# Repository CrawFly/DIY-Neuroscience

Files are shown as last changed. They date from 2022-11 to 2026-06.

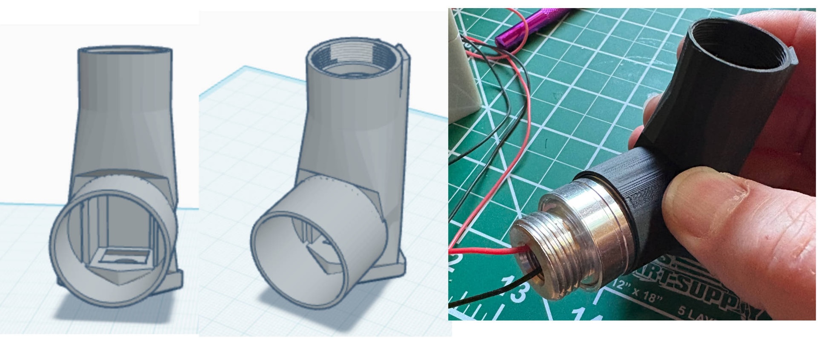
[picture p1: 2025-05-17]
OFM LED parts/OFM LED.jpg

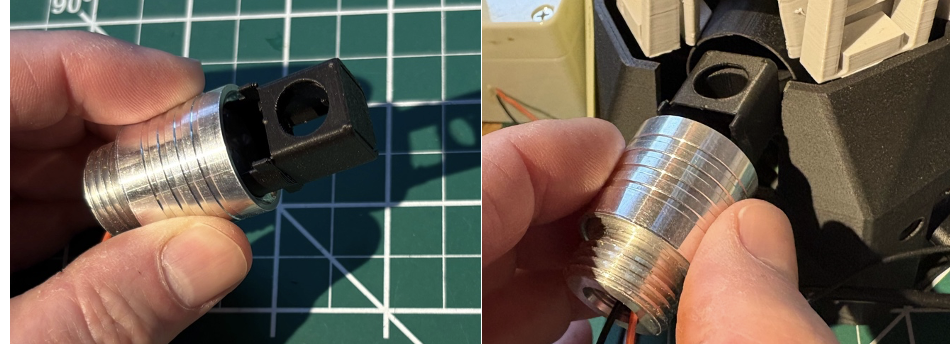
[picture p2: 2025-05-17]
OFM LED parts/OFM LED Filter cube.png

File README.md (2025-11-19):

# DIY-Neuroscience
This is a repository for storing code, stl files, and build instructions for DIY neuroscience equipment designed and built by faculty at Cornell University and Hobart &amp; William Smith Colleges.

Build videos for the micromanipulator builds can be found on our YouTube Channel at:
https://www.youtube.com/@jimryan4024
These build videos are too large to include here.

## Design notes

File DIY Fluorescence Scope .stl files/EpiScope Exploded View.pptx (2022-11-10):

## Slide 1

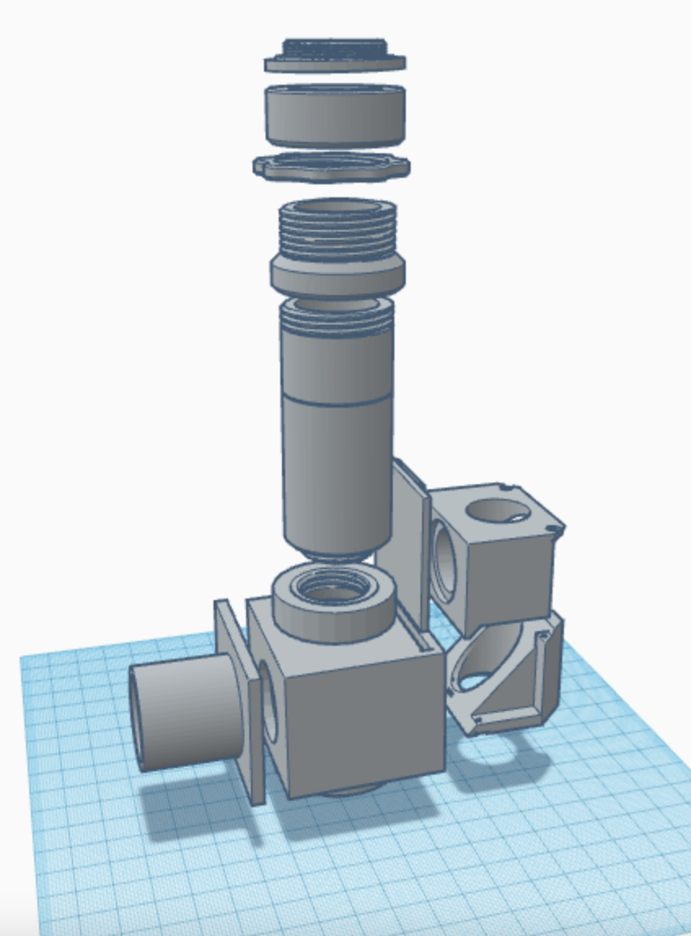
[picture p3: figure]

EpiScope
Exploded View

C-Mount Collar (B)

C-Mount Lock Nut (C)

Tube Extender Ring (D)

Microscope Tube (E)

Filter Cube Door (J)

Microscope Tube
Lower Adapter (F)

Filter Cube Top (K)

LED Tube (I)

Filter Cube
Holder (G)

Filter Cube Bottom (L)

RMS Objective
Lens Adapter (H)

C-Mount Thread (A)

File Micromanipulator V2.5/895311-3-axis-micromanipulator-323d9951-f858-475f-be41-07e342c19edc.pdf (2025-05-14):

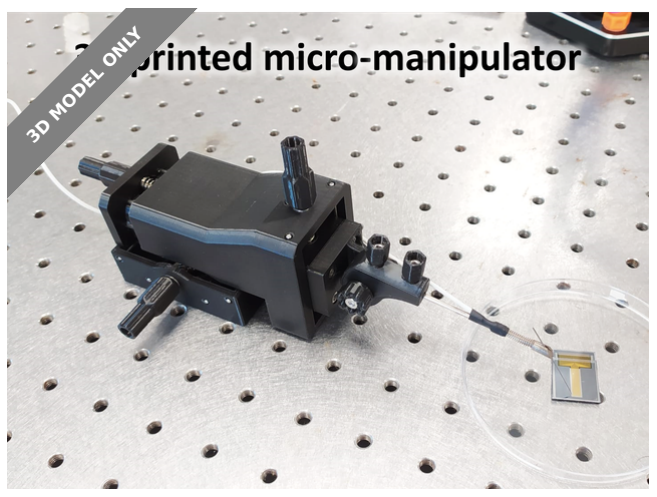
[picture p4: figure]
3D MODEL ONLY

## Summary

This design is a micromanipulator designed to precisely handle tools at the micron scale

Hobby & Makers (https://printables.com/model?categoryId=48) > Tools (https://printables.com/model?categoryId=49)

Tags: | precision | linearmotion | handler | micron | manipulator
micromanipulator | microscopic

Micromanipulators are tools designed to precisely handle objects at the micron scale. They are very important in science as they allow to interact directly with microscopic device, when direct manual handling would most likely result in destruction. However, professional quality micromanipulator can be very expensive (thousands of USD), out of reach of hobbyists and sometimes a scarce resource even for professional researchers.

This is my take at designing a high quality micromanipulator. The result is stiff, compact and moves smoothly. Not quite up to par with the commercial alternatives, but fit for most applications and accessible for a handful of USD and half an hour of your time.

The complete build process is described in detail in an instructable:

https://www.instructables.com/Build-a-3D-Printed-Micro-manipulator/

RemiRafael (https://printables.com/@RemiRafael)

## 3 axis micromanipulator

VIEW IN BROWSER (https://printables.com/model/895311-3-axis-micromanipulator)

updated 29. 5. 2024 | published 29. 5. 2024

## Model files

micromanipulator-z-slider.stl

micromanipulator-middle.stl

micromanipulator-base.stl

straight-holder-base.stl

straight-holder-arm.stl

micromanipulator-top.stl

straight-holder-knob.stl

knob.stl

cutting-guide-micromanipulator.stl

## License

This work is licensed under a
Creative Commons (4.0 International License)

Attribution-NonCommercial (http://creativecommons.org/licenses/by-nc/4.0/)

✖ | Sharing without ATTRIBUTION
✔ | Remix Culture allowed
✖ | Commercial Use
✖ | Free Cultural Works
✖ | Meets Open Definition

holder-knob.stl

90-holder.stl

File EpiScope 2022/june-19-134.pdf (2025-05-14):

The Journal of Undergraduate Neuroscience Education (JUNE), Fall 2020, 19(1):A134-A140

JUNE is a publication of Faculty for Undergraduate Neuroscience (FUN) www.funjournal.org

## ARTICLE Building Your Own Neuroscience Equipment: A Precision Micromanipulator and an Epi-fluorescence Microscope for Calcium Imaging

### James Ryan¹, Bruce R. Johnson², and David Deitcher²

1Biology Department, Hobart and William Smith Colleges, Geneva, NY 14456; 2Department of Neurobiology and Behavior, Cornell University, Ithaca, NY 14853.

A faculty member’s ability to develop meaningful research-oriented laboratories in neurobiology is often hampered by
the rapid pace of new technologies and the increasing cost of equipment. To help undergraduate neuroscience faculty meet these challenges, we introduce two important neuroscience research tools we designed and built. The first is a precision micromanipulator for neurophysiology applications costing less than $40 USD. We compare data generated using the DIY manipulator with commercial micromanipulators costing over $1000. The second tool is our newly designed 3D printed epi-fluorescence microscope. Commercial fluorescence imaging devices often cost over $20,000, but our 3D printed version is constructed for less than $1200. This epi-fluorescence microscope uses interchangeable LED light sources and filter sets to image static fluorescence in prepared slides and calcium imaging of neuronal activity in living Drosophila brains. This later technique uses transgenic flies with a genetically encoded calcium indicator, GCaMP, linked to green fluorescent protein (GFP). During an action potential, calcium ions (Ca²⁺) enter neurons and are observed as an increase in fluorescence intensity from a series of video images. These neuronal firing patterns can be assessed qualitatively and quantitatively to understand neural circuits leading to specific behaviors. We plan to develop curricula around the use of the epi-fluorescence microscope for calcium imaging in the next year, and to provide detailed parts sources and construction guides for the student and faculty DIY experience.

Key words: micromanipulator; neurophysiology; epsp; epi-fluorescence; GFP; mCherry; GCaMP; Calcium imaging

This report is based on our presentation at the 2020 FUN Virtual Meeting where we introduced two new teaching and research tools for undergraduate neuroscience faculty. The rapid pace of new technologies and the increasing cost of equipment can restrict the development of meaningful research-oriented laboratories in neuroscience. However, the present availability of inexpensive industrial parts, efficient supply chains for parts distribution, 3-D printing and open source software development can facilitate faculty development of do-it-yourself (DIY) laboratory teaching and research tools to overcome curricular and research financial limitations.
Previously the Cornell Hoy Neurobiology group and collaborators have designed a variety of inexpensive or free tools for neuroscience teaching and research laboratories. These include an extracellular amplifier (Land et al., 2001), suction electrodes (Land et al., 2001; Johnson et al., 2007), a temperature control device (Krans and Hoy, 2005), micromanipulators (Krans et al., 2006), physiological stimulators (Land et al., 2004), LED control boxes for optogenetic stimulation (Pulver et al., 2010; Vilinsky et al., 2018), and electrophysiological data acquisition and analysis software (Lott et al., 2009). Here we describe our
recent | progress | developing | an | inexpensive
micromanipulator for student neurobiology teaching labs and research, and an inexpensive fluorescence imaging device for dynamic and static fluorescence visualization. Precision micromanipulators from commercial sources cost ~$500 to over $1000 USD. The one described below can be constructed by faculty or students for about $40.00 in parts. Fluorescence microscopes with imaging cameras are expensive, often costing over $20,000 each. This cost often puts fluorescence microscopes out of reach for many undergraduate neuroscience courses and faculty/student research. Our imaging microscope can be constructed using about $1200 in parts. A major goal for our DIY work is to increase the toolbox for neuroscience teaching, learning and research for students and faculty, especially at national and foreign institutions with limited financial resources.

### DIY EQUIPMENT

Precision Micromanipulator Design
We designed an inexpensive micromanipulator that student lab teams could assemble from a kit and use for any laboratory exercise or research that requires fine probe placement. The precision micromanipulator can be built in approximately one hour. It consists of two modified x-y microscope stages, several 3D printed parts, and various nuts and bolts (Figure 1). The two x-y mechanical stages can be purchased online (Amazon, eBay) for under $20USD each. These stages have movement range of 60mm x 30mm and an accuracy of 0.1mm. The manipulator is constructed by first removing the slide holders from both x-y stages and then removing the y-axis from the x-axis on one of the two stages. The single x-axis is joined to the other x-y stage using an aluminum L-bracket with M3 screws and nuts. Finally, the completed x-y-z stage is epoxied and

Ryan et al. | DIY Neuroscience Equipment | A135

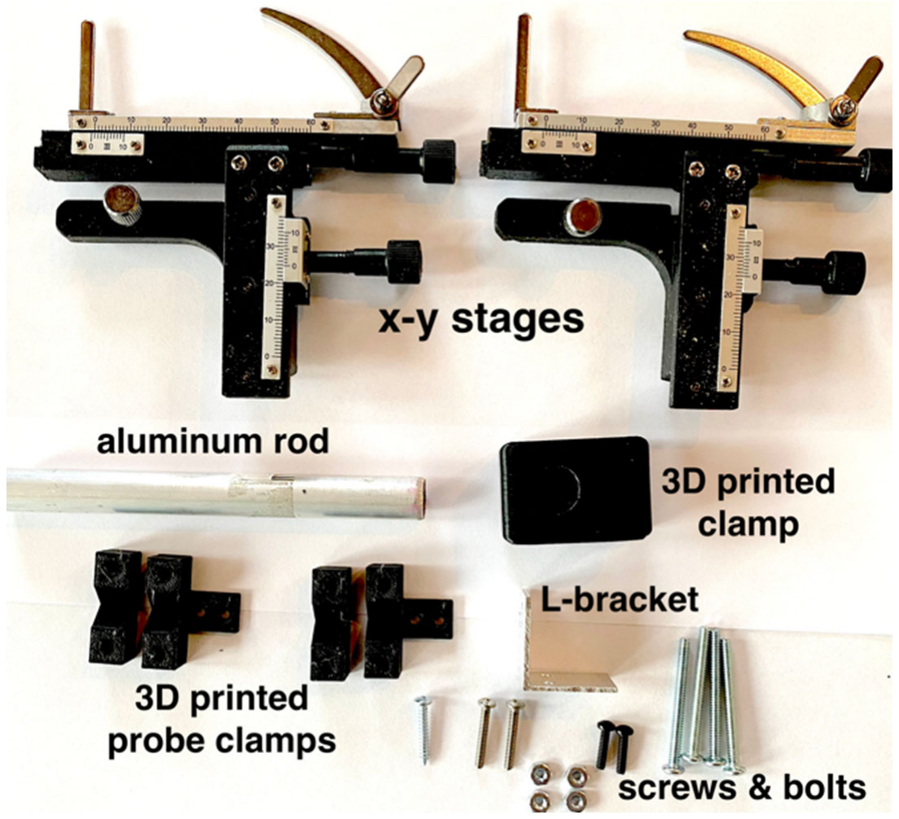
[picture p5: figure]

Figure 1. The components for assembling the DIY precision micromanipulator. There are 2 x-y mechanical stages, an aluminum rod and L-bracket, a set of 3D printed parts, and miscellaneous nuts and bolts for assembly.

screwed into the 3D printed manipulator clamp. The 3D printed parts include a manipulator clamp, a thumb screw housing, and a set of 4 probe holder clamps (Figure 2). These parts are printed from .stl files using PLA, ABS, or similar filaments at 80% infill for added strength. The .stl files can be sent to a local 3D printer or uploaded to an online printing service such as CraftCloud. The 3D printed thumb screw is both threaded into the M6 hex cap and epoxied in place. The completed thumb screw is then threaded into a nut housed inside the 3D printed manipulator clamp. We are preparing parts lists, construction manuals and videos for future dissemination.

DIY Micromanipulator Performance
We compared the stability and fine movement accuracy of our DIY manipulator with a much more expensive (~$1300) Narishige M333 micromanipulator that is normally used for student electrophysiological recordings in the “Principles of Neurophysiology“ laboratory class at Cornell University (BioNB4910). A conventional electrophysiological rig (Wyttenbach et al., 2018) with 2 A-M Systems Model 1600 intracellular amplifiers, an ADInstruments Power Lab for data acquisition with LabChart software, and glass intracellular microelectrodes filled with 3M KCl (resistances 15-20 MOhm) were used to record and display the membrane potentials from crayfish muscle fibers. We recorded intracellular excitatory synaptic potentials (EPSPs) from two different crayfish superficial flexor (SF) muscle fibers with electrodes and amplifier headstages clamped to our DIY and the Narishige manipulators. Details of the saline composition, dissection and recording protocols for crayfish muscle are found in the Crawdad lab manual (Wyttenbach et al., 2014)
Figure 3 shows EPSPs recorded simultaneously from different muscle fibers using the two manipulators. Both muscle fibers were easily penetrated, and both recordings were stable and of similar fidelity. Thus, the DIY manipulator has the precision and stability to record intracellular potentials. The EPSP amplitudes recorded with the Narishige M333 micromanipulator (blue trace) have higher amplitudes than those recorded with our DIY manipulator (red trace), probably because the electrode of the blue recording was closer to a synaptic site. These muscles do not fire action potentials, and EPSP amplitude decays with distance from the synaptic site (Hoyle, 1983). The red and blue recordings in Figure 3 are not the same EPSPs because the SF muscles are poly-neuronally and multiterminally innervated by different, spontaneously active motor neurons (Atwood, 2008).

Epi-fluorescence Microscope Design
The goal here was to design an affordable epi-fluorescence microscope that small student teams could also assemble from a kit and use to bring cutting edge research into the undergraduate neuroscience curriculum. To meet this goal, we designed and built an epifluorescence microscope for approximately $1200 USD. The 3D printed epi-fluorescence microscope described here is suitable for many neuroscience applications including calcium imaging in living neurons.

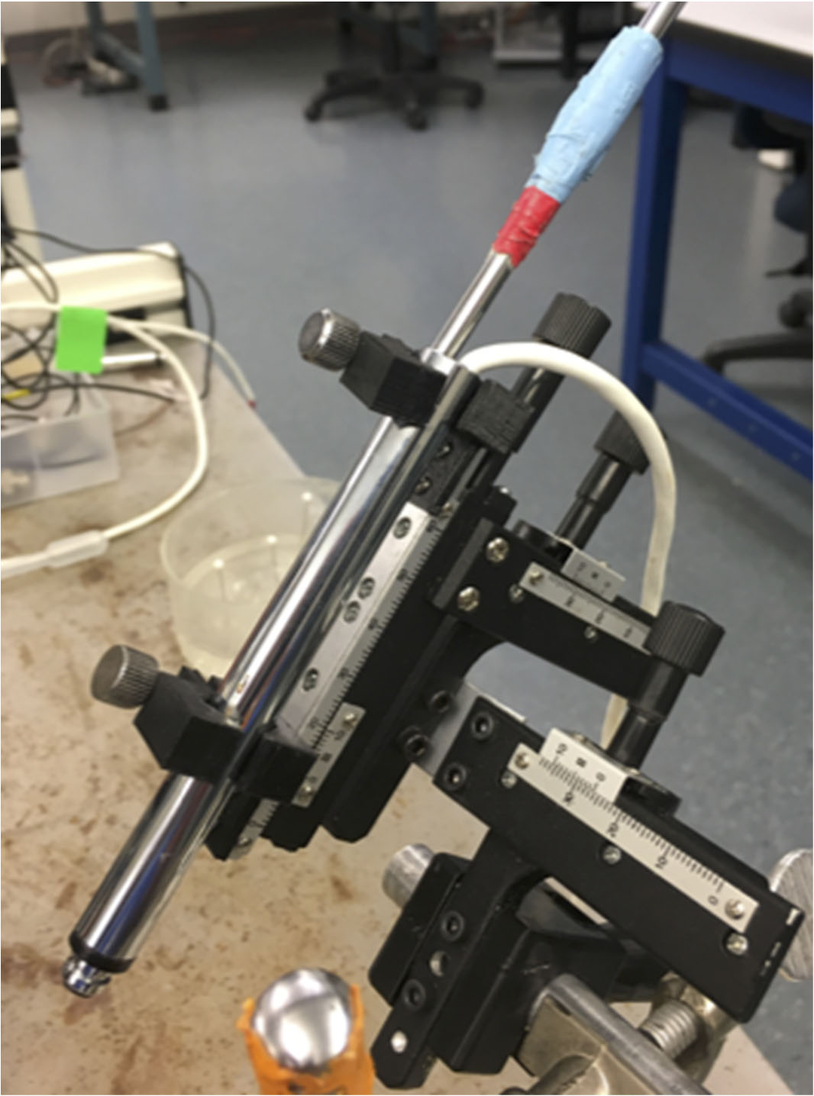
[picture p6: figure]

Figure 2. The fully assembled micromanipulator with intracellular amplifier head-stage clamped in place.

The Journal of Undergraduate Neuroscience Education (JUNE), Fall 2020, 19(1):A134-A140 A136

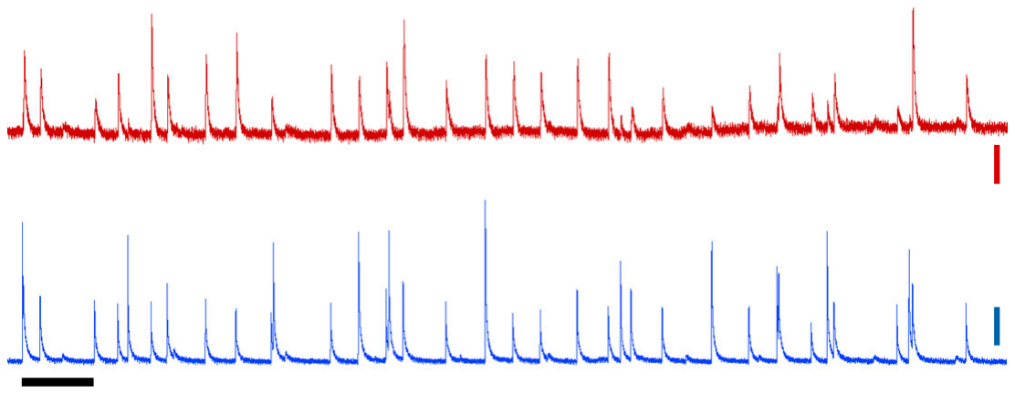
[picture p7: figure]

Figure 3. Simultaneous intracellular recordings of excitatory postsynaptic potential (EPSPs) from 2 different crayfish muscle fibers. Top red trace DIY manipulator; resting potential, -84 mV; calibration bars, 1 mV. Bottom blue trace, Narishige M3330 manipulator; resting potential, -75 mV; calibration bar, 2 mV. Note higher gain in red trace. Horizontal calibration bar, 500 ms.

The scope consists of several off the shelf components coupled with a set of 3D printed parts for the optical housing (Figure 4). The base of the scope is an aluminum optical breadboard drilled for M6 metric threads. Attached to this base is a 2x2 inch extruded aluminum column with t-slots which carries the 3D printed optical components and a precision lab jack for raising and lowering the specimen stage.
Attached to the top of the precision lab jack is a clear plexiglass plate (130 x 190 mm) that holds the specimen slide or dish. Positioning of the specimen in the x-y planes is achieved by a standard x-y mechanical microscope stage mounted to the upper surface of the plexiglass stage. The lab jack allows the entire stage assembly to be lowered easily to replace specimens or add fluids.
On the vertical column, the microscope uses a linear stage with micrometer adjustment for precision focusing the objective lens. Attached to the linear stage is the 3D printed optical housing. The main housing contains the fluorescence filters and has a male c-mount on top for attaching the CMOS camera and a female c-mount on the bottom for the 20x long working distance objective lens. The monochrome global shutter CMOS camera (~$180 from Basler, model da1280-54um/uc) is capable of acquiring images in low light at up to 54 frames per second. This camera has a resolution of 1280x960 pixels and uses a 1/3” Aptina AR0134 sensor. However, any camera with a c-mount can be attached to this port. Inside the main housing is a double filter slider that accepts two sets of fluorescence filters. The excitation and emission filters are 25mm diameter and the dichroic mirror (beamsplitter) is 25.5x36mm. The calcium imaging described below used a single band filter set tailored for green fluorescent protein (GFP) from Iridian Spectral Technologies: 469-35nm excitation, 497nm dichroic mirror, and 525-39nm emission filter ($450 USD). A second filter set for mCherry or Alexa Fluor 595 can be added to the filter slider if desired. In addition, these filter sliders are very inexpensive to 3D print, allowing the user to have several sliders and filter combinations ready to swap out in seconds.
The light source for the scope is an interchangeable highpower LED with heat sink connected to an LED controller box powered by either AC or DC and capable of being driven by a computer stimulus generator via a BNC cable (Figure

4). The wiring diagram for the LED controller has been described previously (Pulver et al., 2011 Vilinsky et al., 2018). For GFP a Cree XLamp XP-E2 high power blue (470nm peak, $4USD, LED Supply.com) LED is coupled to a BuckPuck DC LED driver ($20USD, LEDSupply.com). The LED and a 20mm narrow spot LED lens are housed in a 1 inch diameter aluminum heat sink ($15USD, LEDSupply.com). The LED and its heat sink housing are inserted into the 3D printed LED port. This design allows rapid exchange of different colored LEDs.
The 3D printed parts were designed using the free, online CAD program TinkerCad (AutoDesk). TinkerCad allows you to build complex parts from a library of basic shapes or to import and modify existing .stl files. Finished parts are exported as .stl files for 3D printing (Figure 5). The .stl files can be printed on any 3D printer. However, printing these parts using an online print company such as CraftCloud allow greater choice of print materials. The optical housing described here was printed using MJF Nylon or resin. These materials are stronger and provide higher detail than that of PLA or ABS plastics.
Finally, the microscope is modular in design. Removing the fluorescence filters and adding an LED light source from below the specimen converts the scope into a conventional light microscope. Screw a post and micromanipulator into the base and it becomes a neurophysiology rig.

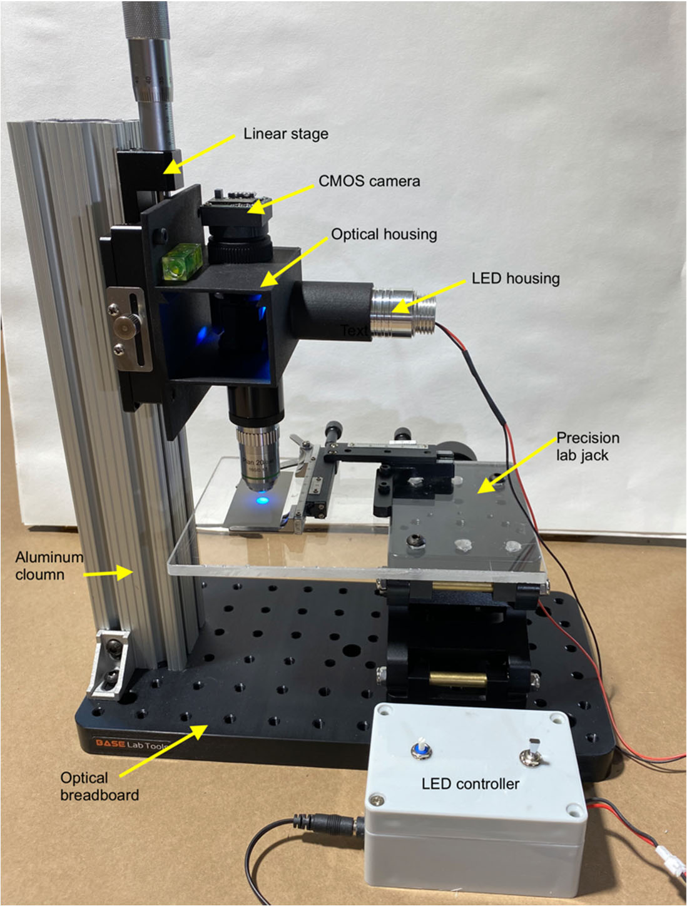
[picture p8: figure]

Figure 4. The epi-fluorescence microscope with LED controller.

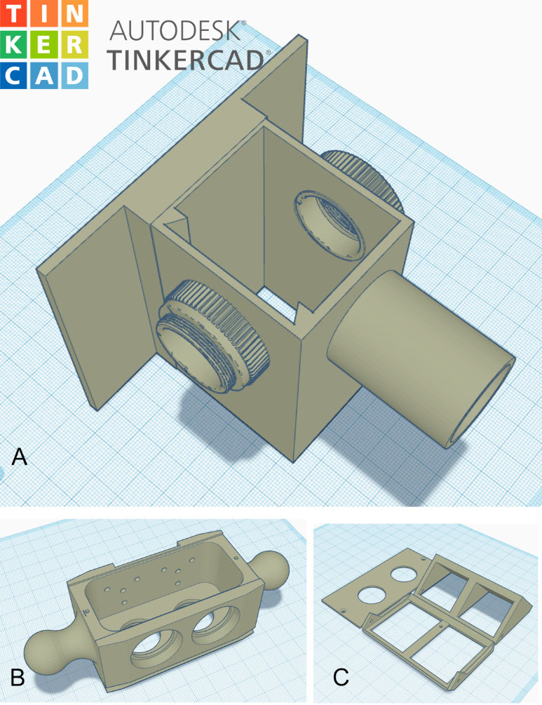
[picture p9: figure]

Figure 5. 3D printable microscope parts shown in TinkerCad prior to export as .stl files. A) Main optical housing, B) Double filter slider, and C) the filter holder components.

Fly Stocks for Imaging Preps
Fluorescent Drosophila lines were raised on standard cornmeal-molasses food. The stocks used were UAS GCaMP7b; P{GMR94G06-GAL4}attP2 for calcium imaging from the Bloomington Stock Center (#80907and #40701) and jus-GAL4 UAS-CD8-GFP (available from D. Deitcher) for static fluorescent imaging of membrane-bound GFP.

Larval and CNS Preparation
Wandering third instar larvae were selected with forceps, placed in a Sylgard petri dish and rinsed with water, then pinned at the mouth hooks and posterior end with fine insect pins with the dorsal (trachea) side oriented up. Room temperature saline (135 mM NaCl, 5 mM KCl, 2 mM CaCl2, 4 mM MgCl2, 5 mM BES, pH 7.5) for calcium imaging was added to the preparation. A superficial incision is made from the tail to the mouth hook with micro-scissors and the “guts” are carefully removed to reveal the CNS composed of brain lobes and ventral ganglion. Additional pins are placed to flatten the cuticle flaps into a “filet” (Pulver et al., 2011). For static fluorescent imaging, the Sylgard disc was adhered to a glass slide with double-sided tape and then imaged using appropriate camera settings. For dynamic calcium imaging, the CNS was excised from the larval filet and gently placed on a Sylgard-coated glass depression slide and covered with saline. The slide was placed on the microscope stage. Initially the camera was set to autoexposure to locate the preparation, then manually adjusted to reveal the GCaMP7b labeled motoneurons.

Flourescent Imaging
To test the epifluorescence microscope, we first attempted to image neurons expressing GFP in the ventral ganglion of the larva. Figure 6 shows static GFP imaging of a ventral ganglion of a third instar larva expressing the membrane-bound GFP fusion, CD8-GFP in selected neurons driven by the GAL4/UAS binary expression system. CD8-GFP is a useful label to highlight the morphology of neurons.
Next, to show the utility of the microscope we imaged a ventral ganglion expressing the calcium-sensitive protein GCaMP7b in a pair of motor neurons in each segment. Images were sent at 10 fps for 300 seconds from the camera to a lap top computer, using camera supplied software, and converted into an AVI format with Fiji (Image J) software. Figure 7 shows two frames of dynamic imaging of actively firing motor neurons in the abdominal ganglia of a fruit fly larvae from the video link (https://youtu.be/zB55QNQ_IrM). For a short while after the larval fly’s CNS is removed, CNS motor networks will produce spontaneous neural activity that is correlated with larval crawling and turning (fictive locomotion, Pulver et al., 2015). Action potential-induced
depolarization | results | in | calcium | entry

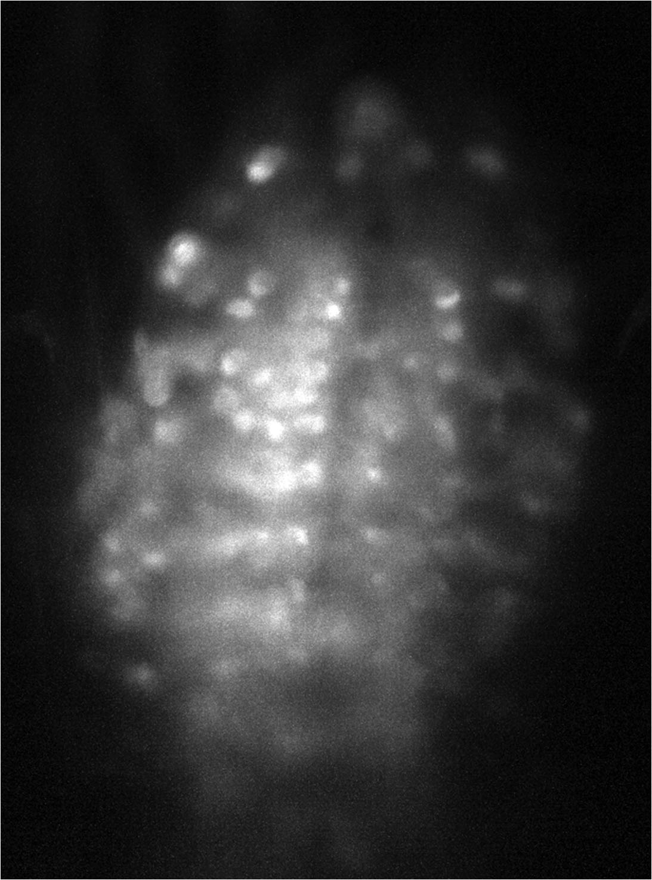
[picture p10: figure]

Figure 6. Expression of membrane-bound GFP in ventral ganglion neurons that express the neural gene, julius seizure (jus).

The Journal of Undergraduate Neuroscience Education (JUNE), Fall 2020, 19(1):A134-A140 A138
which is detected by the genetically encoded calcium indicator, GCaMP that is expressed in selective motoneurons. Thus, calcium-induced fluorescence during neural activity is a proxy for identifying actively firing neurons that normally drive muscles to execute larval locomotion. These neuronal firing patterns can be assessed qualitatively and quantitatively to understand neural circuits leading to specific behaviors.

### DISCUSSION

We present two new teaching and research tools as “proof of concept” of our recent DIY efforts to increase the faculty toolbox for neuroscience teaching, learning and research. Our DIY manipulator performed well compared to the commercial Narishige M333 when recording synaptic potentials. The DIY manipulator could be used for any student lab exercise or research that requires fine probe placement, such as for cell injection of dyes or genetic material. Although students and faculty have not yet formally tested and assessed it, initial and limited feedback for manipulator assembly and use was positive with constructive criticisms from faculty participating in the January 2020 CrawFly workshop in San Antonio. A manipulator made by one of the 2020 CrawFly participants was used to record miniature end-plate potentials from fruit fly larval muscle during the workshop (data not saved). The inexpensive manipulator could expand the range of electrophysiological exercises possible in a student/faculty lab. For example, faculty could add conventional intracellular and whole cell patch recording to student electrophysiology exercises. Our students will construct and use the DIY manipulator for electrophysiological student lab exercises. Learning outcomes, specific student skill objectives, and data analysis suggestions for our electrophysiology exercises are found in the Crawdad lab manual (Wyttenbach et al., 2014).
Our initial results of imaging static GFP fluorescence in fixed tissue and dynamic GFP fluorescence from living neurons during fictive larval locomotion (Pulver et al., 2015) show that our fluorescence microscope is operationally ready to be brought into the student laboratory classroom and into faculty research labs. Any type of fluorescence tissue could be imaged with the appropriate excitation and emission filters. Our fluorescence microscope facilitates unique and high powered research experiences for students and faculty with limited financial resources. We are not the first to propose inexpensive fluorescence imaging for the student neuroscience lab or for research. Our imaging microscope design was inspired by previous efforts including from the “FlyPi” group (Chagas et al., 2017), the miniscope produced by Zhang et al. (2019) and an imaging system recently adapted to a classroom compound microscope (Sane et al., 2020- this JUNE issue). For an imaging microscope design that fit our needs, we searched for the least expensive, yet high quality options for the microscope imaging components, light filters, camera, microscope and mounting stage parts, and JR designed the 3-D printed optical housing, filter holders, and slider.
Our student learning objectives and skills for the imaging

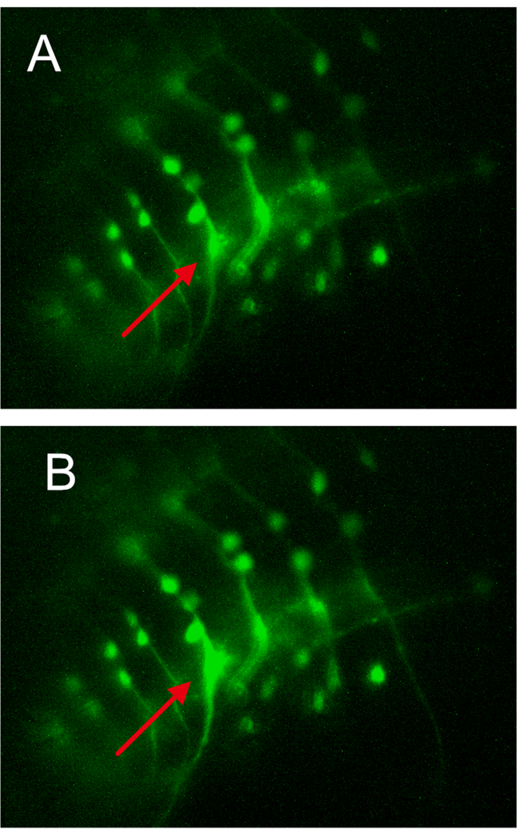
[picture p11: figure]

Figure 7. GCaMP7b fluorescence in select motoneurons of the ventral ganglion. Two single frames taken from series illustrate waves of neural activity during fictive locomotion. A. Earlier fame shows cell at red arrow with low light intensity. B. Later frame shows higher intensity light emission from the same neuron, indicating greater electrical excitability. See short video link (https://youtu.be/zB55QNQ_IrM) for entire series of images.

microscope and dynamic imaging project will promote interdisciplinary thinking and skills in our neuroscience students. For example, they will study the excitable properties of neurons though calcium imaging as a proxy for signal transmission by action potentials, and the advantages of imaging for exploring neuronal circuit activity (Yang and Yuste, 2017). Students will examine the properties of light and optics, and understand principles of fluorescence imaging (Cox, 2012) as they build and use their imaging microscopes to measure fluorescence in living preparations expressing fictive locomotion. They will learn introductory coding to control camera software and analyze images, and practice engineering design and construction by building the microscope. This includes 3D printing, soldering, fine scale assembly, and troubleshooting. Finally, students will perfect their dissection and dexterity skills by preparing Drosophila larval nervous systems for imaging.
We are still preparing imaging analysis protocols appropriate for our undergraduate student use. μManager software can be used to gather the imaging movies from the camera, and image J to process the images and select “regions of interest”. Data analysis programs such as
Dataview | (Heitler, | 2009; | https://www.st-
andrews.ac.uk/~wjh/dataview/) can be used to visualize and measure fluorescent amplitude and activity patterns (see Sane et al., 2020, this JUNE issue). Our imaging software protocols, in prep, will be designed for student interaction to modify Python code at various phases of image acquisition, analysis and visualization.
We hope that our goals for the imaging microscope project in particular will be broadly applicable at other institutions. The National Research Council (2003) emphasizes that future science research progress will require greater STEM interdisciplinary training. We plan to create an interdisciplinary classroom where students from different STEM studies work together to develop the confidence to build and understand equipment and solve biological problems. Interdisciplinary science education is considered critical for the future recruitment of talented scientists (Kazar and Elrod, 2012). Our imaging project promotes interdisciplinary learning with engineering design, physics (optics and light principles), biology (genetics and neuroscience), and computer science (introductory coding to control camera software and analyze images). Teambased learning skills required for research (Bennett and Gadlin, 2012) will be fostered as student teams build, test, and trouble shoot their own instrumentation, and gather and analyze data to answer biological questions. Too often our students treat instrumentation as a “black box”, with little understanding of how scientific equipment works. We are in the process of developing written and video guides for construction and use of the manipulator and the imaging microscope, along with laboratory modules to guide inquiry driven research experiences for students (Fromherz et al., 2018).
Our plans for a Spring 2020 rollout of student team construction and use of the manipulator and imaging microscope in the laboratory classroom were derailed by the Covid-19 pandemic, but we will continue our curriculum development for both Cornell and Hobart and William Smith students this Spring 2021. We will follow inclusive classroom practices of clearly structured assignments and expectations, and emphasize that all ideas are welcome, respected and open for discussion (Penner, 2018). We will assess student interdisciplinary awareness (Basu et al., 2017; Crisp and Muir, 2012) before and after imaging microscope use, and student perceived experience and confidence in building and using the imaging microscope (Glover and Luzon, 2018). Our student learning outcomes will be examined by grading student mastery of microscope construction, designing and testing hypotheses of neuronal network activity through data gathering and interpretation, student written journal-like articles and oral presentations on their work. Our project results will be disseminated through additional journal articles and faculty workshops such as

CrawFly
(https://www.adinstruments.com/training/education/application-workshops?field_event_type_tid=2977).

### REFERENCES

Atwood HL (2008) Parallel ‘phasic’ and ‘tonic’ motor systems of the crayfish abdomen. J Exp Biol 211:2193-2195.
Basu,A, Mondoux MA, Whitt JL, Isaacs AK, Narita T (2017) Integrative approach to STEM concepts in an introductory neuroscience course: Gains in interdisciplinary awareness. J Undergrad Neurosci Educ 16(1):A102-A111.
Bennett ML, Gadlin H (2012) Collaboration and team science: From theory to practice. JIM 60:768-775.
Chagas AM, Prieto-Godino LL, Arrenberg AB, Baden B (2017) The €100 lab: A 3D- printable open-source platform for fluorescence microscopy, optogenetics, and accurate temperature control during behaviour of zebrafish, Drosophila, and Caenorhabditis
elegans. | PLoS | Biol | 15(7):e2002702.
https://doi.org/10.1371/journal. pbio.2002702.
Cox G (2012) Fluorescence and fluorescence microscopy. In: Optical imaging techniques in cell biology pp 35-48. Boca Raton, FL: CRC Press LLC.
Crisp KM, Muir GM (2012) Assessing development of an interdisciplinary perspective in an undergraduate neuroscience course. J Undergrad Neurosci Educ 10(2):A88-95.
Fromherz S, Whitaker-Fornek J, Andrew A. Sharp AA (2018) Classroom-based research experiences to support underserved STEM student success: From introductory inquiry to optogenetics in the embryonic chicken. J Undergrad Neurosci Educ 17(1):A97-A110.
Glover EM, Lauzon O (2018) Using a contrast illusion to teach principles of neural processing. J Undergrad Neurosci Educ 17(1):A81-A88.
Heitler WJ (2009) Practical tools for analysing rhythmic neural
activity. | J | Neurosci | Methods | 185:151-64. | doi:
10.1016/j.jneumeth.2009.09.009
Hoyle G (1983) Muscles and their neural control pp 483-525. New York, NY: John Wiley and Sons.
Johnson BR, Hauptman SA, Bonow RH (2007) Construction of a simple suction electrode for extracellular recording and Stimulation. J Undergrad Neurosci Educ 6(1):A21-A26.
Kazar A, Elrod S (2012) Facilitating interdisciplinary learning: Lessons from Project Kalioedoscope. Change 44(1): 16-25. Krans JL, Hoy RR (2005) Tools for physiology labs: An inexpensive means of temperature control. J Undergrad Neurosci Educ 4(1):A22-A26.
Krans J, Gilbert C, Hoy R (2006) Teaching insect retinal physiology with newly designed, inexpensive micromanipulators. Adv Physiol Educ 30:254-261.
Land BR, Wyttenbach RA, Johnson BR (2001) Tools for the student physiology lab: An inexpensive high-performance amplifier and suction electrode for extracellular recording. J Neurosci Meth 106:47-55.
Land BR, Johnson BR, Wyttenbach, RA, Hoy RR (2004) Tools for Physiology Labs: Inexpensive equipment for physiological stimulation. J Undergrad Neurosci Educ 3:A30-A35.
Lott GK III, Johnson BR, Bonow R H, Land BR, Hoy RR (2009) g-PRIME: A free, windows based data acquisition and event analysis software package for physiology in classrooms and research labs. J Undergrad Neurosci Educ 8(1):A50-A54. National Research Council (2003) BIO2010: Transforming undergraduate education for future research biologists.
Available | at | https://www.nap.edu/catalog/10497/bio2010-
transforming-undergraduate-education-for-future-researchbiologists.
Penner MR (2018) Building an inclusive classroom. J Undergrad

The Journal of Undergraduate Neuroscience Education (JUNE), Fall 2020, 19(1):A134-A140 A140

Neurosci Educ 16(3):A268-A272.
Pulver SR, Hornstein NJ, Land BL, Johnson BR (2011)
Optogenetics | in | the | teaching | laboratory: | Using
channelrhodopsin-2 to study the neural basis of behavior and synaptic physiology in Drosophila. Adv Physiol Educ 35(1):82-91.
Pulver SR, Bayley TG, Taylor AL, Berni J, Hedwig B (2015) Imaging fictive locomotor patterns in larval Drosophila. J Neurophysiol 114(5):2564-77.
Booth JRH, Sane V, Gather M, Pulver SR (2020) Inexpensive Methods for Live Imaging of Central Pattern Generator Activity in the Drosophila Larval Locomotor System. J Undergrad Neurosci Educ 19(1):A124-A132.
Vilinsky.I, Hibbard KL, Johnson BR, Deitcher DL (2018) Probing synaptic transmission and behavior in Drosophila with optogenetics: A laboratory exercise. J Undergrad Neurosci Educ 16 (3):A289-A295.
Wyttenbach RA, Johnson BR, Hoy RR. (2014) Crawdad: An Online Lab Manual for Neurophysiology Sinauer Associates, Inc., Sunderland, MA.
Wyttenbach RA, Johnson BR, Hoy RR (2018) Reducing the cost of electrophysiology in the teaching laboratory. J Undergrad

Neurosci Educ 16 (3):A277-A281.Yang W, Yuste R (2017) In
vivo | imaging | of | neural | activity. | Nat
Methods 14(4):349-359. doi: 10.1038/nmeth.4230.
Zhang L, Bo Liang B, Barbera G,1, Hawes S, Zhang Y, Stump K, Baum I, Yang Y, Li Y, Lin D-T (2019) Miniscope GRIN lens system for calcium imaging of neuronal activity from deep brain structures in behaving animals. Curr Protocols Neurosci 86:e56. doi: 10.1002/cpns.56.

Received September 22, 2020; accepted October 22, 2020.

This work was funded by a grant from the Cornell Center for Teaching Innovation (DD and BRJ), and support from Hobart-William Smith Colleges (JR). We thank Dr. Stefan Pulver of the University of St. Andrews in Scotland for DIY inspiration and advice.

Address correspondence to: Dr. James Ryan, Biology Department, Hobart and William Smith Colleges, Geneva, NY 14456. Email: ryan@hws.edu

Copyright © 2020 Faculty for Undergraduate Neuroscience www.funjournal.org

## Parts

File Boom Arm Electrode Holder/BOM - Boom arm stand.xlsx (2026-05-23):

Boom arm stand for Electrodes
Qty | Price $ | Total $ | Description | Source | Notes
2 | $19.59 | $39.18 | x-y microscope stage | https://www.amazon.com/Microscope-Moveable-Mechanical-Professional-Attachable/dp/B0D4ZL1B7J | Or similar
1 | $17.50 | $17.50 | 1/8th inch thick metal plate- 4x4inch | https://www.amazon.com/Weldable-Rolled-Steel-Plate-Square/dp/B0B4BT4M38 | Sold as a 2 pack
1 | $12.99 | $12.99 | magnetic base | https://www.harborfreight.com/multi-position-magnetic-base-with-fine-adjustment-63663.html | optional if using metal plate
1 set | varies | varies | 3D printed parts | https://github.com/CrawFly/DIY-Neuroscience | Cost varies - but less than $3
1 |  |  | 6 inch coated copper magnet wire 28ga | https://www.amazon.com/dp/B07P2H6KR5?ref=ppx_yo2ov_dt_b_fed_asin_title&th=1 | You only need about 6 inches
1 |  |  | 6 inch bare copper wire 24 ga | https://www.amazon.com/HWYEE-24Gauge-electroculture-Gardening-187FT/dp/B0F5Q8WBFD | You only need about 6 inches
1 | $0.35 | 0.35 | 20ga dispensing needle | https://www.amazon.com/dp/B07QQ59JL6?ref=ppx_yo2ov_dt_b_fed_asin_title&th=1
1 | $1.17 | $1.17 | stereo audio female jack with wire | https://www.amazon.com/dp/B082VVWND3?ref=ppx_yo2ov_dt_b_fed_asin_title
 |  | $71.19

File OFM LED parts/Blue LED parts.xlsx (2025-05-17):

 | LED 470nm
1 | Luxeon rebel or Cree 470nm Blue LED | $7.33 | $7.33 | https://www.ledsupply.com/leds/cree-xlamp-xp-e2-color-high-power-led-star
1 | Carclo lens -frosted narrow spot | $1.25 | $1.25 | https://www.ledsupply.com/led-optics/10194-carclo-lens-frosted-narrow-spot-led-optic
1 | heat sink 1 up LED Housing | $10.99 | $10.99 | https://www.ledsupply.com/led-heatsinks/dynamic-led-heatsink-housing
1 | Dimmable BuckPuck 1000mA | $14.99 | $14.99 | https://luxeonstar.com/product/3023-d-e-1000/
1 | Project box (or equivalent) | $4.41 | $4.41 | https://www.amazon.com/BUD-Industries-CU-1874-B-Plastic-Utility/dp/B005T5CZHC?fst=as%3Aoff&rnid=1243644011&s=hi
1 | 12volt 1amp wall wart for LED with barrel jack | $6.99 | $6.99 | https://www.amazon.com/inShareplus-Mounted-Switching-100-240V-Connector/dp/B01GD4ZUCY?s=electronics
 |  | TOTAL | $38.97

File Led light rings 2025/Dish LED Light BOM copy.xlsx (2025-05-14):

LED lights for CrawFly
Qt | Description | Cost per item | Cost total | Source | Notes
3D Printed files
1 | Dish ring led.stl | $0.38 | $0.38 | Available online at Github | These can be printed locally or you can upload the stl files to craftcoud - an online printing service and they will print the parts and send them to you. It's more expensive but still not too bad.
1 | Scope ring led.stl | $0.38 | $0.38 | Available online at Github | Printed at 15% infill
1 | Switch box top.stl | $0.11 | $0.11 | Available online at Github
1 | Switch box bottom.slt | $0.50 | $0.50 | Available online at Github
4 | M4 screw caps.stl | $0.13 | $0.52 | Available online at Github
1 | Soldering fingers.stl (Optional) | $0.52 | $0.52 | Available online at Github | Optional
 |  |  | $0.00
Hardware
2 | 10.5 inch COB led strip | $1.00 | $2.00 | https://www.amazon.com/dp/B089NNF3FB?ref=ppx_yo2ov_dt_b_fed_asin_title&th=1 | only need about 2 feet - so you can make 8 sets from one 16 foot strip
2 | 20mm circular rocker switches | $1.00 | $2.00 | https://www.amazon.com/dp/B082NWF69K?ref=ppx_yo2ov_dt_b_fed_asin_title&th=1 | or similar
6 feet | double-stranded wire | $0.16 | $0.96 | https://www.amazon.com/hz/mobile/mission | Comes in a 100ft spool fpr $16
3 | Barrel jacks - male and female prewired | $0.95 | $2.85 | https://www.amazon.com/dp/B072BXB2Y8?ref=ppx_yo2ov_dt_b_fed_asin_title
3 | barrel jacks - female for box | $0.40 | $1.20 | https://www.amazon.com/dp/B08CVCJ97Q?ref=ppx_yo2ov_dt_b_fed_asin_title&th=1
1 | 12V 1amp wall power supply | $3.80 | $3.80 | https://www.amazon.com/dp/B00FEOB4EI?ref=ppx_yo2ov_dt_b_fed_asin_title&th=1
1 | 12V Battery unit for AA batteries | $4.00 | $4.00 | https://www.amazon.com/dp/B00VE7HBMS?ref=ppx_yo2ov_dt_b_fed_asin_title | Optional
4 | M4 x 20mm socket head screws | $0.12 | $0.48 | https://www.amazon.com/dp/B07CJL1ZZN?ref=ppx_yo2ov_dt_b_fed_asin_title&th=1 | or similar source
4 | M4 inserts | $0.10 | $0.40 | https://www.amazon.com/dp/B0CS6XGMFD?ref=ppx_yo2ov_dt_b_fed_asin_title&th=1
2 | 12mmx2mm rare earth magnets | $0.11 | $0.22 | https://www.amazon.com/TRYMAG-Magnets-Neodymium-Refrigerator-Whiteboard/dp/B0CHVPD4K8?s=industrial | Optional
 |  |  | $0.00
 |  |  | $0.00
Tools required
1 | soldering iron with solder and M4 insert adapter
1 | hot glue gun with glue sticks
1 | super glue
1 | wire cutter/stripper
1 | scissors
 |  | Total | $20.32

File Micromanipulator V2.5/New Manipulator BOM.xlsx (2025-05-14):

Item | Description | Qt | Cost each | Total Cost | total $ | Source | Comments
post | 1/2 inch diameter steel rod - 4 inch long | 1 | $1.00 | $1.00 | $8.98/ 3 ft | Lowes or Home Depot | Must be cut to length with hack saw or metal saw
post plate | 1.5 x 2.5 x 1/8 inch steel bar | 1 | $2.00 | $2.00 | $21.27/ 3ft | Lowes or Home Depot | Must be cut to length with hack saw or metal saw
metal epoxy | Steel Stick epoxy putty | 1 | $6.54 | $6.54 | $6.54 | Lowes or Home Depot | enough to build about 8 micromanipulator posts
regular epoxy | gray quick set 2-part epoxy | 1 | $7.98 | $7.98 | $7.98 | Lowes or Home Depot | enough to build about 8 micromanipulator posts
M6 screws | M6 x 10 or M6x15mm screws | 4 | $0.72 | $2.88 | $7.29/ 10pk | https://www.amazon.com/J-B-Weld-8267-SteelStik-Reinforced/dp/B00RN7CT2U?mcid=867bbe140d5435f788c74a3f6edfd631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
3D Printed Files
Mount for base | stl file | 1 | ? |  |  | Can be printed in PLA locally | See 3D printer instructions and files
manipulator base | stl file | 1 | ? |  |  | Can be printed in PLA locally
X-axis | stl file | 1 | ? |  |  | Can be printed in PLA locally
Y-axis | stl file | 1 | ? |  |  | Can be printed in PLA locally
Z-axis | stl file | 1 | ? |  |  | Can be printed in PLA locally
Rod measuring guage | stl file | 1 | ? |  |  | Can be printed in PLA locally
Probe base | stl file | 1 | ? |  |  | Can be printed in PLA locally
probe holder | stl file | 1 | ? |  |  | Can be printed in PLA locally
probe clamps | stl file | 2 | ? |  |  | Can be printed in PLA locally
Hardware
x-axis M3 screw |  | 1 | $0.17 | $0.17 | $8.50/ 50pk | https://www.amazon.com/dp/B089KRYJ9Q?ref=ppx_yo2ov_dt_b_fed_asin_title&th=1 | These come in packages of 50 and may be cheaper to buy from MacMaster Carr by the piece
y-axis M3 screw |  | 1 | $0.18 | $0.18 | $8.78/ 50pk | https://www.amazon.com/dp/B089KS7KKN?ref=ppx_yo2ov_dt_b_fed_asin_title&th=1 | These come in packages of 50 and may be cheaper to buy from MacMaster Carr by the piece
z-axis M3 screw |  | 1 | $0.19 | $0.19 | $9.36/ 50 pk | https://www.amazon.com/dp/B089KS7KKN?ref=ppx_yo2ov_dt_b_fed_asin_title&th=1 | These come in packages of 50 and may be cheaper to buy from MacMaster Carr by the piece
x-axis compression spring | 304 Stainless Steel, 7mm OD, 0.8mm Wire Size, 35mm Free Length | 1 | $0.27 | $0.27 | $2.72/ 10pk | https://www.amazon.com/Diameter-Stainless-Compression-Spring-Length/dp/B0B7DWP7JD
y-axis compression spring | 304 Stainless Steel, 7mm OD, 0.8mm Wire Size, 40mm Free Length | 1 | $1.23 | $1.23 | 6.19 / 5pk | https://www.amazon.com/dp/B0C33CNMPC?ref=ppx_yo2ov_dt_b_fed_asin_title&th=1
z-axis compression spring | 305 Stainless Steel, 7mm OD, 0.8mm Wire Size, 40mm Free Length | 1 | $0.27 | $0.27 | $2.72/ 10pk | https://www.amazon.com/Diameter-Stainless-Compression-Spring-Length/dp/B0B7DYBD94
2mm brass or steel rod | 2mm x 305mm brass or steel rods | 5 | $2.49 | $12.45 | $9.99/ 20pk | https://www.amazon.com/dp/B09WKL554D?ref=ppx_yo2ov_dt_b_fed_asin_title&th=1
M4 brass insert | Brass inserts M4 | 11 | $0.10 | $1.10 | $9.99/ 100pk | https://www.amazon.com/dp/B0CS6XGMFD?ref=ppx_yo2ov_dt_b_fed_asin_title&th=1
M4 hex socket head screws |  | 3 | $0.08 | $0.24 | $7.79/ 100pk | https://www.amazon.com/uxcell-Socket-M4-0-7x12-Stainless-Silver/dp/B0DDJBKC6D?s=industrial&sp_csd=d2lkZ2V0TmFtZT1zcF9hdGY
x-y microscope stage |  | 1 | $25.00 | $25.00 | $25.00 | https://www.amazon.com/OMAX-Mechanical-Stage-Biological-Microscope/dp/B00FG88P3A?gQT=1 | remove the y-axis and other components - see instructions
M4 washers |  | 2 | $0.04 | $0.08 | $3.57/100pk | https://www.mcmaster.com/products/washers/system-of-measurement~metric/screw-size~m4/washers-2~/
M3 nuts |  | 3 | $0.03 | $0.09 | $2.62/100pk | https://www.mcmaster.com/products/nuts/hex-nuts-3~/system-of-measurement~metric/hex-nuts-3~hex-nut-profile~standard/thread-size~m3/
Base (optional) | Base Labs 150x150mm optical base | 1 | $46.00 | $46.00 | $46.00 | https://www.baselabtools.com/150mm-x-150mm-Solid-Aluminum-Optical-Breadboard_p_351.html
Total |  |  |  | $107.67
Tools
hack saw (or dremel tool)
drill
metric allen wrenchs
soldering iron with insert attachment

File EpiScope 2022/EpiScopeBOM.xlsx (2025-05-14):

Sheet: June version
 | MICROSCOPE
Quantity | Description | Unit cost | Total cost | Source
1 | BoliOptics 20x infinity corrected long working distance objective | $149.98 | $149.98 | https://bolioptics.com/20x-infinity-corrected-long-working-distance-plan-achromatic-microscope-objective-lens-working-distance-5-1mm/
1 | X Linear Stage, 60x60mm w/ Micrometer | $46.29 | $46.29 | https://www.amazon.com/gp/product/B07TP397F5
1 | Basler global shutter monochrome camera w/ software | $179.00 | $179.00 | https://www.mouser.com/ProductDetail/Basler/106681
1 | MicroB to USB3.0 cable | $6.99 | $6.99 | https://www.amazon.com/AmazonBasics-USB-3-0-Cable-Male/dp/B00NH12R1O?s=electronics
1 | 470/40x emission filter |  | $450.00 | Iridian GFP filter set =$450. https://www.iridian.ca/product/gfp-filter-set/
1 | 495 Dichroic mirror |  | $0.00
1 | 525/50 Dichroic mirroe |  | $0.00
1 | 2x2" aluminum extrusion - 36in * enough for 3 scopes | $22.57 | $22.57 | https://www.amazon.com/gp/product/B00BMUW2WG/ref=ppx_yo_dt_b_asin_title_o00_s00?ie=UTF8&psc=1
2 | Aluminum right angle connector (4pack) | $7.99 | $15.98 | https://www.amazon.com/gp/product/B076D76YDD/ref=ppx_yo_dt_b_asin_title_o01_s00?ie=UTF8&psc=1
1 | Aluminum plate 6x12 inch 1/4in thick Metric M6 | $104.00 | $104.00 | http://www.baselabtools.com/150mm-x-300mm-x-20mm-Thick-Aluminum-Breadboard_p_609.html
1 | M4-0.7MM Pitch Nylock Nylon Locking Nuts (100) | $8.99 | $8.99 | https://www.amazon.com/gp/product/B07LCPGPJ8/ref=ppx_yo_dt_b_asin_title_o02_s00?ie=UTF8&psc=1
1 | 1.5mm x 25M Clear Double Sided Strong Adhesive Tape | $6.75 | $6.75 | https://www.amazon.com/gp/product/B06Y2YHWT9/ref=ppx_yo_dt_b_asin_title_o05_s00?ie=UTF8&psc=1
1 | 25mm long C-mount extensin tube | $30.00 | $30.00 | https://www.edmundoptics.com/p/25mm-length-c-mount-extension-tube/15553/
1 | C-mount to RMS/DIN adapter | $35.00 | $35.00 | https://www.edmundoptics.com/p/c-mount-to-din-objective-ring-mount-03627/93/
1 | 5 3D printed parts |  |  | cost depends on how they are printed (~ $35)
 |  | TOTAL | $1055.55
 | LED 470nm
1 | Lueon rebel 447.5nm Royal Blue LED w/ 9o optic 700mA | $7.33 | $7.33 | https://www.ledsupply.com/leds/luxeon-rebel-color-leds
1 | Carclo lens -frosted narrow spot | $1.25 | $1.25 | https://www.ledsupply.com/led-optics/10194-carclo-lens-frosted-narrow-spot-led-optic
1 | heat sink 1 up LED Housing | $10.99 | $10.99 | https://www.ledsupply.com/led-heatsinks/dynamic-led-heatsink-housing
1 | wire harness for BuckPuck | $4.99 | $4.99 | https://www.luxeonstar.com/wiring-harness-for-buckpuck-drivers-6-wire-with-pot
1 | Dimmable BuckPuck 1000mA | $14.99 | $14.99 | https://www.luxeonstar.com/1000ma-externally-dimmable-buckpuck-dc-driver
1 | Project box (or equivalent) | $4.41 | $4.41 | https://www.amazon.com/BUD-Industries-CU-1874-B-Plastic-Utility/dp/B005T5CZHC?fst=as%3Aoff&rnid=1243644011&s=hi
1 | 12volt 1amp wall wart for LED with barrel jack | $6.99 | $6.99 | https://www.amazon.com/inShareplus-Mounted-Switching-100-240V-Connector/dp/B01GD4ZUCY?s=electronics
 |  | TOTAL | $43.96
 | STAGE
1 | X-Y Stage for microscope slides | $10.91 | $10.91 | https://www.amazon.com/gp/product/B07G71M9QC/ref=ppx_yo_dt_b_asin_title_o07_s00?ie=UTF8&psc=1
1 | Acrylic sheet (black) 1/4in thick 12x12 *enough for 2 stages | $16.72 | $16.72 | https://www.amazon.com/RMP-Aluminum-Sheet-0-125-Thickness/dp/B00HRHB5XA
6 | M4 screws 20mm
1 | Precision Lab Jack | $120.00 | $120.00 | https://www.amazon.com/Precise-Platform-Elevator-Optical-PT-SD408/dp/B079989RX9
 | TOTAL | TOTAL | $147.63
 |  |  | $0.00
Misc Items
 | allen wrech set (metric)
 | Metric tap set
 | silicone wire
 | soldering station
 | M4,5,6 screws and nuts
 | Windows 10 laptop
 | small screw diver set
 | 3D printer microscope parts
 | Loctite gel super glue
 | drill press or hand drill
 | hack saw or band saw
Alternatives | Optional items
1 | Spinel Global Shutter Cmos Camera UC10MPC_ND | $62.00 | $62.00 | https://store.spinelelectronics.com/index.php?route=product/search&search=global%20shutter
1 | Z axis linear stage 60x60 w/ micromter | $70.00 | $70.00 | https://www.amazon.com/dp/B06X9RK9XL
1 | BA2/M mounting base | $7.52 | $7.52 | https://www.thorlabs.de/newgrouppage9.cfm?objectgroup_id=47&pn=BA2#2978
1 | TR40/M 40mm post | $5.12 | $5.12 | https://www.thorlabs.de/newgrouppage9.cfm?objectgroup_id=1266&pn=TR40/M#1270
1 | PH30/M post holder | $7.24 | $7.24 | https://www.thorlabs.de/thorproduct.cfm?partnumber=PH30/M

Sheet: New version
 | MICROSCOPE
Quantity | Description | Unit cost | Total cost | Source
1 | BoliOptics 20x infinity corrected long working distance objective | $149.98 | $149.98 | https://bolioptics.com/20x-infinity-corrected-long-working-distance-plan-achromatic-microscope-objective-lens-working-distance-5-1mm/
1 | X Linear Stage, 60x60mm w/ Micrometer | $46.29 | $46.29 | https://www.amazon.com/gp/product/B07TP397F5
1 | Basler global shutter monochrome camera w/ software | $179.00 | $179.00 | https://www.mouser.com/ProductDetail/Basler/106681
1 | MicroB to USB3.0 cable | $6.99 | $6.99 | https://www.amazon.com/AmazonBasics-USB-3-0-Cable-Male/dp/B00NH12R1O?s=electronics
1 | 470/40x emission filter |  | $450.00 | Iridian GFP filter set =$450. https://www.iridian.ca/product/gfp-filter-set/
1 | 495 Dichroic mirror |  | $0.00
1 | 525/50 Dichroic mirroe |  | $0.00
1 | Aluminum sliding table | $45.00 | $45.00 | https://www.amazon.com/gp/product/B08JXCMPFX/ref=ppx_yo_dt_b_asin_title_o03_s00?ie=UTF8&th=1
1 | Aluminum plate 6x12 inch 1/4in thick Metric M6 | $104.00 | $104.00 | http://www.baselabtools.com/150mm-x-300mm-x-20mm-Thick-Aluminum-Breadboard_p_609.html
1 | M4-0.7MM Pitch Nylock Nylon Locking Nuts (100) | $8.99 | $8.99 | https://www.amazon.com/gp/product/B07LCPGPJ8/ref=ppx_yo_dt_b_asin_title_o02_s00?ie=UTF8&psc=1
1 | 1.5mm x 25M Clear Double Sided Strong Adhesive Tape | $6.75 | $6.75 | https://www.amazon.com/gp/product/B06Y2YHWT9/ref=ppx_yo_dt_b_asin_title_o05_s00?ie=UTF8&psc=1
1 | 3D printed parts |  |  | cost depends on how they are printed (~ $35-70)
 |  | TOTAL | $997.00
 | LED 470nm
1 | Lueon rebel 447.5nm Royal Blue LED w/ 9o optic 700mA | $7.33 | $7.33 | https://www.ledsupply.com/leds/luxeon-rebel-color-leds
1 | Carclo lens -frosted narrow spot | $1.25 | $1.25 | https://www.ledsupply.com/led-optics/10194-carclo-lens-frosted-narrow-spot-led-optic
1 | heat sink 1 up LED Housing | $10.99 | $10.99 | https://www.ledsupply.com/led-heatsinks/dynamic-led-heatsink-housing
1 | wire harness for BuckPuck | $4.99 | $4.99 | https://www.luxeonstar.com/wiring-harness-for-buckpuck-drivers-6-wire-with-pot
1 | Dimmable BuckPuck 1000mA | $14.99 | $14.99 | https://www.luxeonstar.com/1000ma-externally-dimmable-buckpuck-dc-driver
1 | Project box (or equivalent) | $4.41 | $4.41 | https://www.amazon.com/BUD-Industries-CU-1874-B-Plastic-Utility/dp/B005T5CZHC?fst=as%3Aoff&rnid=1243644011&s=hi
1 | 12volt 1amp wall wart for LED with barrel jack | $6.99 | $6.99 | https://www.amazon.com/inShareplus-Mounted-Switching-100-240V-Connector/dp/B01GD4ZUCY?s=electronics
 |  | TOTAL | $43.96
 | STAGE
1 | X-Y Stage for microscope slides | $10.91 | $10.91 | https://www.amazon.com/gp/product/B07G71M9QC/ref=ppx_yo_dt_b_asin_title_o07_s00?ie=UTF8&psc=1
 |  |  |  | Misc M3, M4, M5 bolts as specificed in the build powerpoint and fast setting epoxy
 | TOTAL | TOTAL | $10.91
 |  |  | $0.00
Misc Items
 | allen wrech set (metric)
 | Metric tap set
 | silicone wire
 | soldering station
 | M4,5,6 screws and nuts
 | Windows 10 laptop
 | small screw diver set
 | 3D printer microscope parts
 | Loctite gel super glue
 | drill press or hand drill
 | hack saw or band saw

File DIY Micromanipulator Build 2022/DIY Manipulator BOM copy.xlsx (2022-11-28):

DIY Micromanipulator Bill of Materials
Quantity | Item | $ each | total $ | Source
1 | Clamp holder (.stl file) | $12.00 | $12.00 | 3D printed by CraftCloud - upload .stl file to CraftCloud select ABS material and 20% infill - use 60% infill for a stonger part - ORDER IN BULK TO SAVE
1 | Probe holder set (2 pairs) (.stl file) | $11.00 | $11.00 | 3D printed by CraftCloud - upload .stl file to CraftCloud select ABS material and 20% infill - ORDER IN BULK TO SAVE
2 | x-y mechanical stages | $15.00 | $30.00 | https://www.amazon.com/Oranmay-Microscope-Attachable-Mechanical-High-Precision/dp/B07G71M9QC?cv_ct_cx=x-y+mechanical+stage&s=industrial
1 | Aluminum L-bracket | NA | NA | 3/4" wide cut from a longer piece of 1x1" L-channel by hand - L-channel is 1/8th inch thick (from Lowes or HomeDepot)
4 | 4-40 machine screw (philips head) with nut 1/2 inch long | $0.05 | $0.20
4 | 6-32 machine screws (philips head) 1.5 inch long | $0.20 | $0.80
4 | 6-32 wing nuts | $0.48 | $1.92
1 | Round Aluminum Rod or Tube, 1/2" diameter and 5-6 inches long | $5.10 | $5.10 | can purchase from Lowes or Home Depot (https://www.amazon.com/gp/product/B07KY9GNZY)
2 | #4 x 3/4 inch sheet metal screws - philips head | $0.03 | $0.06
 |  |  | $0.00
 |  |  | $0.00
 |  | Total | $61.08 | this price will be less if 3D printed items are purchased in bulk
Tootls Needed
1 | cordless drill
1 | 1/8th inch drill bit
1 | 7/64 inch drill bit
1 | 3/32 inch drill bit
1 | PH 1 philips head screw driver |  |  | jewers size to fit tiny screws on x-y stages - any brand will do, but here's an exmple: https://www.amazon.com/Wera-05118023001-Screwdriver-Electronic-Applications/dp/B00725BUIM?s=industrial
1 | PH 2 philips head screw driver |  |  | to fit the 1/8 inch bolts and screws - this is a normal small philips head screw driver
1 | small needlenose pliers |  |  | anything similar to this: https://www.amazon.com/Performance-Tool-1105-Long-Pliers/dp/B002KS96SW?s=industrial
1 | epoxy 2-part set |  |  | Anything similar to this - https://www.amazon.com/J-B-Weld-8265S-Cold-Weld-Reinforced/dp/B0006O1ICE?s=industrial or this which has a shorter hardening time: https://www.amazon.com/J-B-Weld-8276-KwikWeld-Reinforced/dp/B0006O1ICY
1 | fine tipped mechanical pencil |  |  | for marking holes onto L-bracket -anything similar to this: https://www.amazon.com/PENTEL-Mechanical-Drafting-Pencil-P209BP2K6/dp/B002VKWSYI

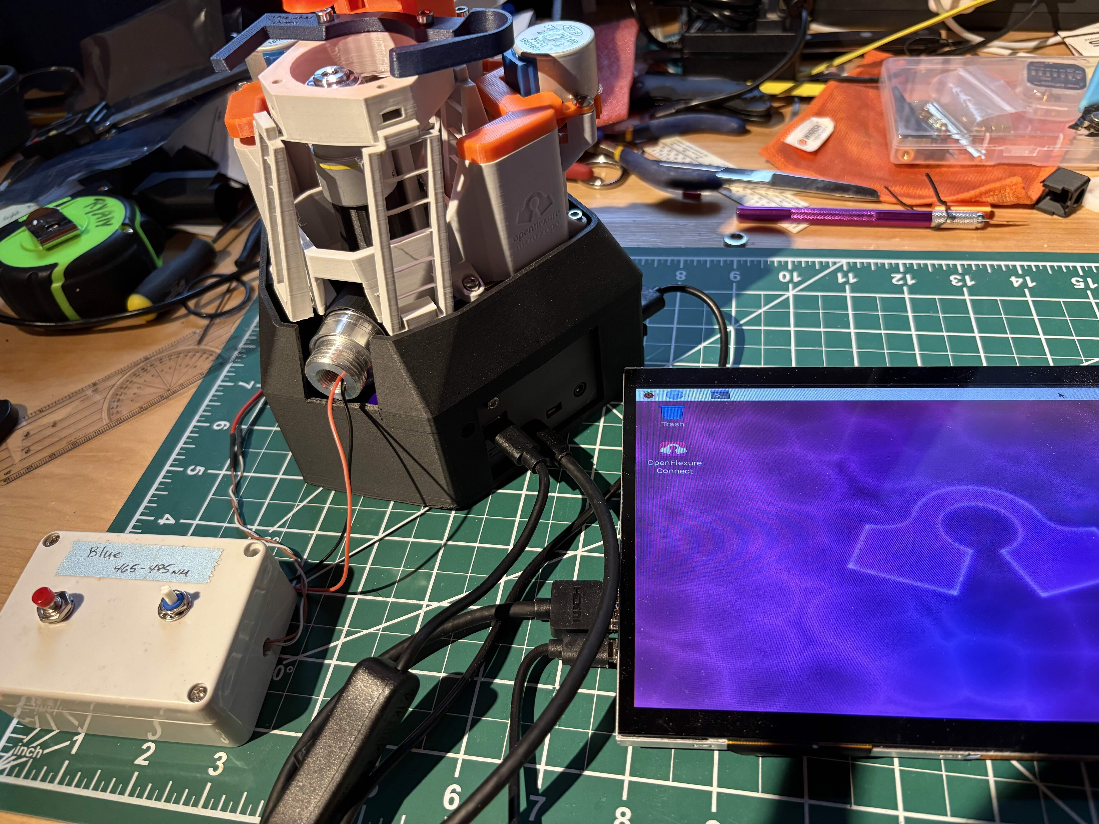
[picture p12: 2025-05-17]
OFM LED parts/OFM with Led.jpg

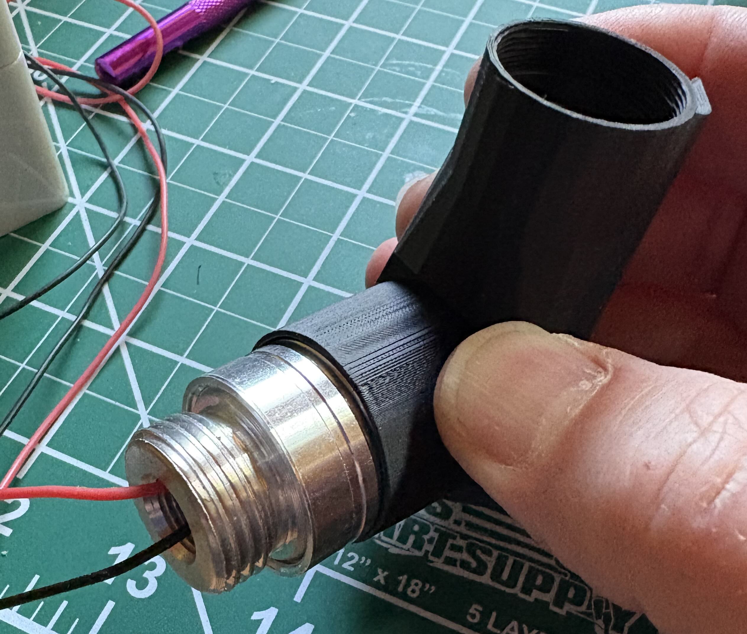
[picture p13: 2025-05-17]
OFM LED parts/LED OFM.jpg

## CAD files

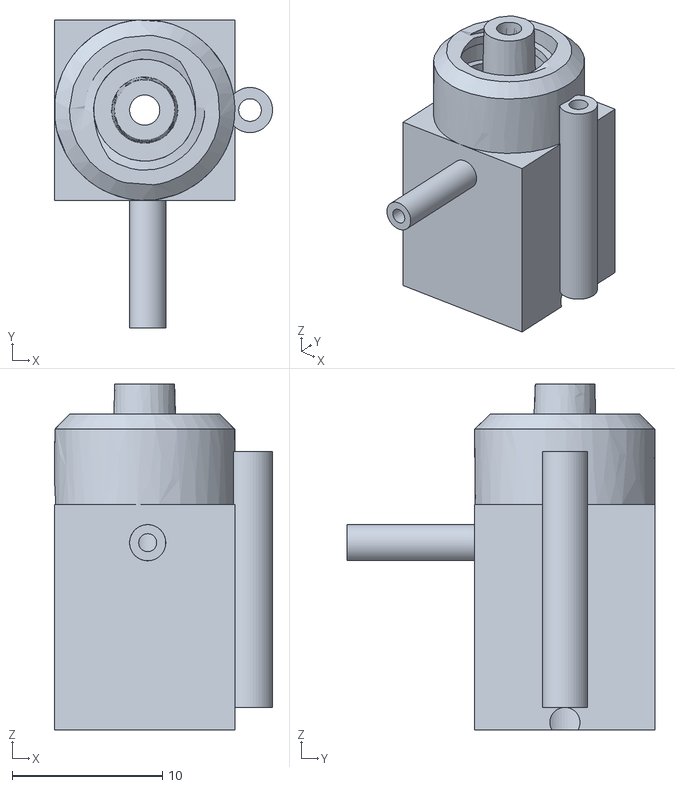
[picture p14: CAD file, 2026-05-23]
Boom Arm Electrode Holder/Electrode Part C suction.stl
14.5 x 20.5 x 23.0

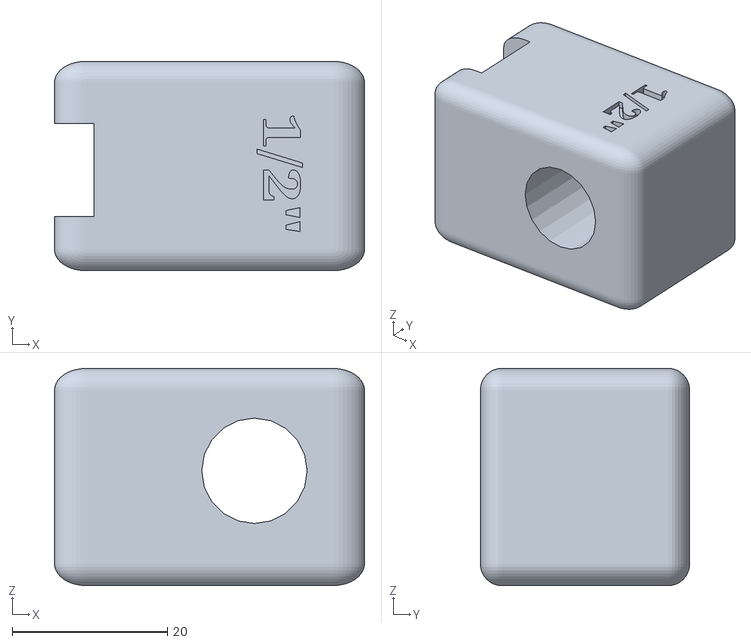
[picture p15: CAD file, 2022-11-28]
DIY Micromanipulator Build 2022/Final ManipulatorBase copy.stl
40.0 x 27.0 x 28.0

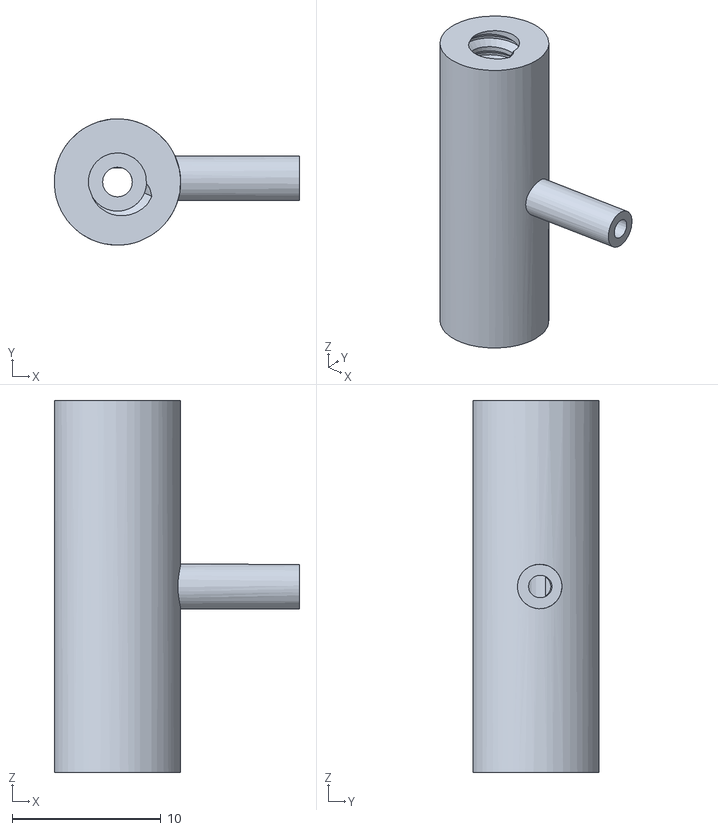
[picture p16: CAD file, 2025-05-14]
electrode holder 2025/electrode holder 2025-3.stl
16.5 x 8.50 x 25.0

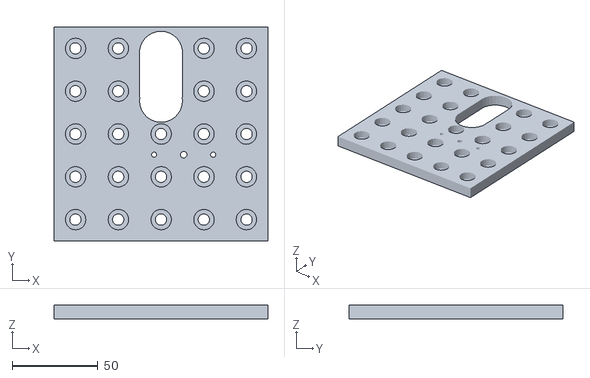
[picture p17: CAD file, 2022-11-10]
EpiScope stl files/ScopeStageV3.stl
125.0 x 125.0 x 8.00

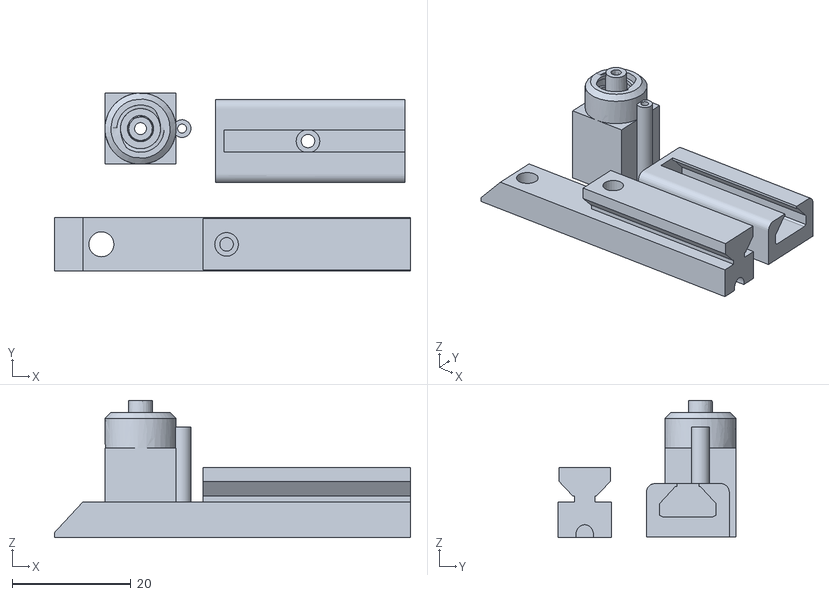
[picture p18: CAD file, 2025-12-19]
Extracellular Pin Electrodes/Pin Electrode Holder-3.stl
60.0 x 30.0 x 23.1

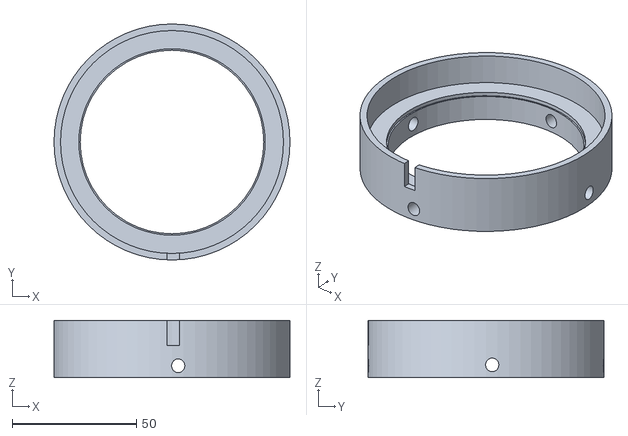
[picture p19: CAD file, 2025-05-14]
Led light rings 2025/Scope ring led.stl
95.0 x 95.0 x 23.0

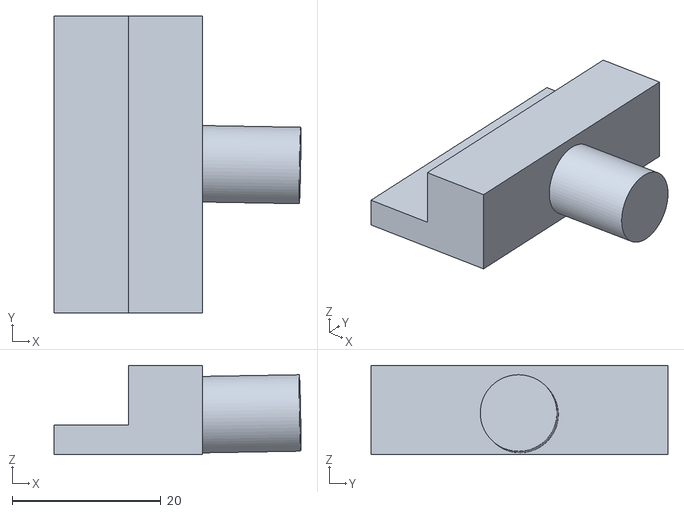
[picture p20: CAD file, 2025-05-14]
Micromanipulator V2.5/Probe holder parts 1.stl
33.2 x 40.0 x 12.0

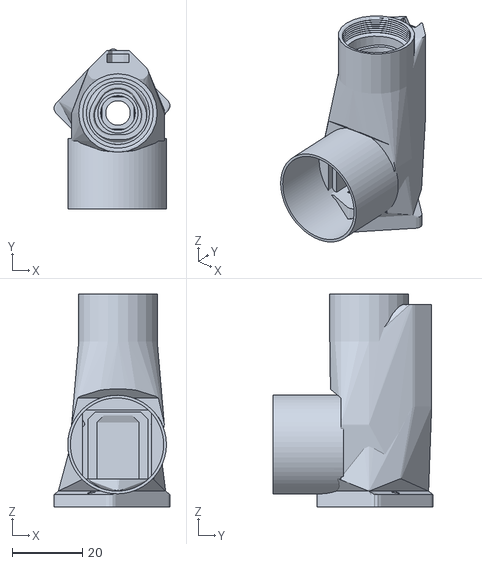
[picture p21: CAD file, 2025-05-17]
OFM LED parts/OpenFlexure Epi-LED holder.stl
32.9 x 45.4 x 60.5

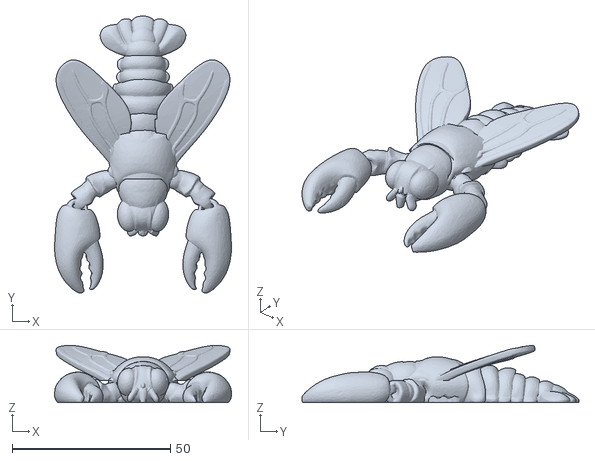
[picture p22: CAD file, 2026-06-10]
Surprising Curcan-3.stl
56.0 x 87.6 x 18.1

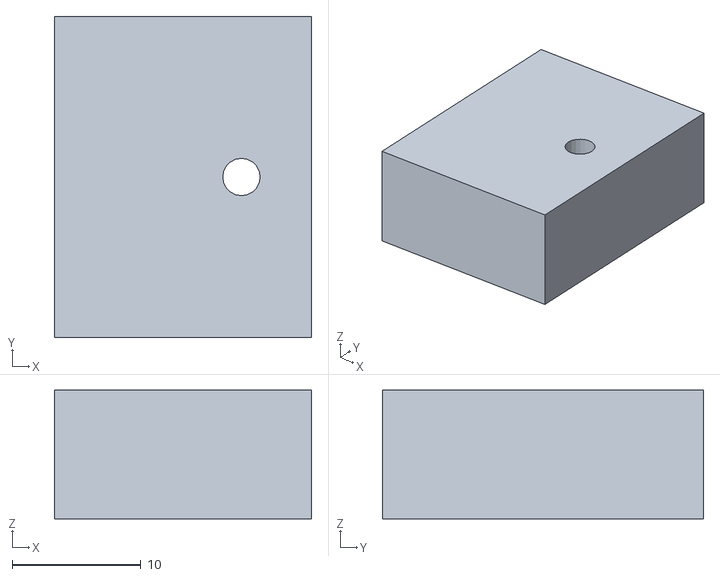
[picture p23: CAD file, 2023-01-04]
Tiny Micromanipulator/Tiny Manipulator Parts-3.stl
20.0 x 25.0 x 10.0

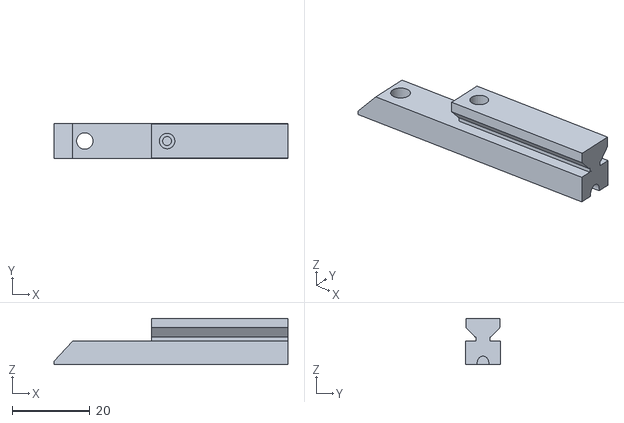
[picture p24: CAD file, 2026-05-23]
Boom Arm Electrode Holder/Electrode Part B.stl
60.0 x 9.00 x 11.8

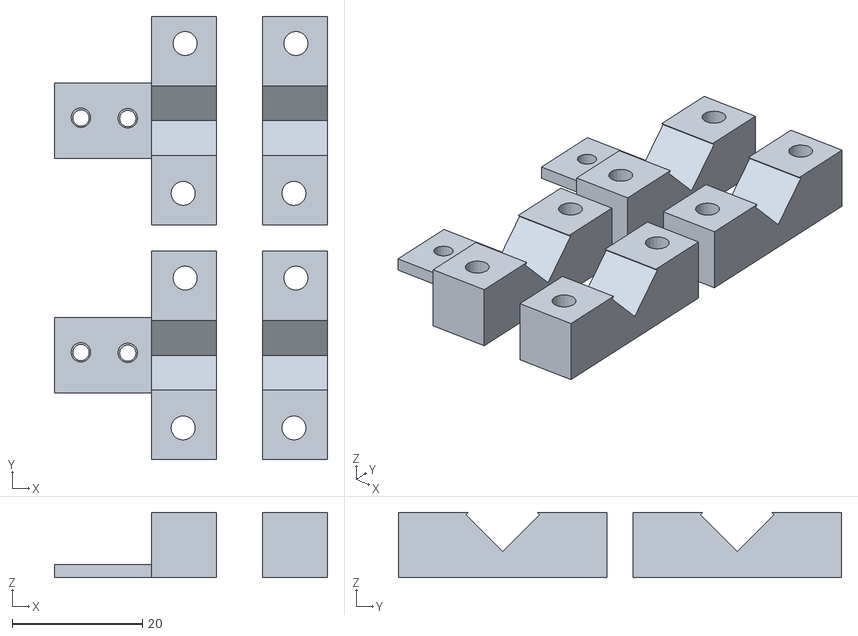
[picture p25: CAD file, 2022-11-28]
DIY Micromanipulator Build 2022/Probe holders copy.stl
41.9 x 68.0 x 10.0

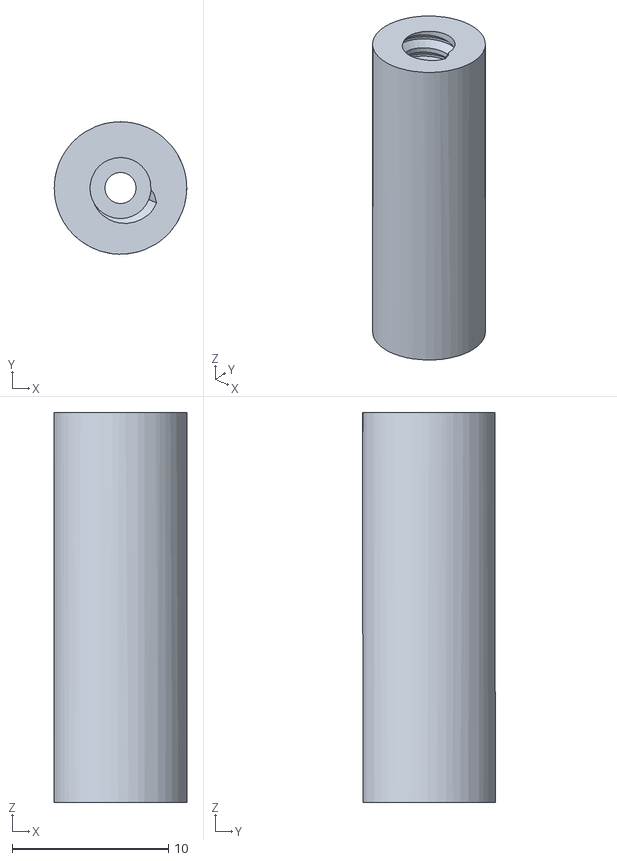
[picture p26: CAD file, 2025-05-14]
electrode holder 2025/electrode holder 2025-2.stl
8.50 x 8.50 x 25.0

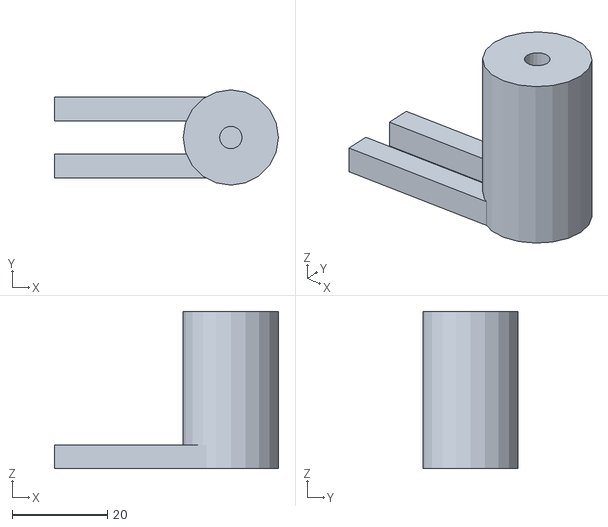
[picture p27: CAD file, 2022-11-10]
EpiScope stl files/Stage%20Supports.stl
47.0 x 20.0 x 33.0

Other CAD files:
Micromanipulator V2.5/cutting-guide-micromanipulator.stl
OFM LED parts/OpenFlexure Epi-LED holder-3.stl
Tiny Micromanipulator/Tiny Manipulator Parts-2.stl
Boom Arm Electrode Holder/Electrode Part C.stl
Boom Arm Electrode Holder/Electrode Part A.stl
Boom Arm Electrode Holder/Part A.stl
Boom Arm Electrode Holder/Part B.stl
Boom Arm Electrode Holder/Part C.stl
Boom Arm Electrode Holder/Part D.stl
Boom Arm Electrode Holder/Part E.stl
Boom Arm Electrode Holder/Part F.stl
Boom Arm Electrode Holder/Part G.stl
EpiScope stl files/0V1iPtvsOvW-2.stl
EpiScope stl files/0V1iPtvsOvW.stl
EpiScope stl files/C-Mount%20Collar%20(B).stl
EpiScope stl files/C-Mount%20Lock%20NUt%20(C).stl
EpiScope stl files/C-Mount%20Thread%20(A).stl
EpiScope stl files/Cool%20Stantia.stl
EpiScope stl files/Course%20Mount.stl
EpiScope stl files/CourseFocusKnob.stl
EpiScope stl files/FilterCubeDoor.stl
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

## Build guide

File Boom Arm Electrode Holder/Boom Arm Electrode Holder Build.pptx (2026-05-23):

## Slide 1

Building the Boom Arm Extracellular Electrode Holder

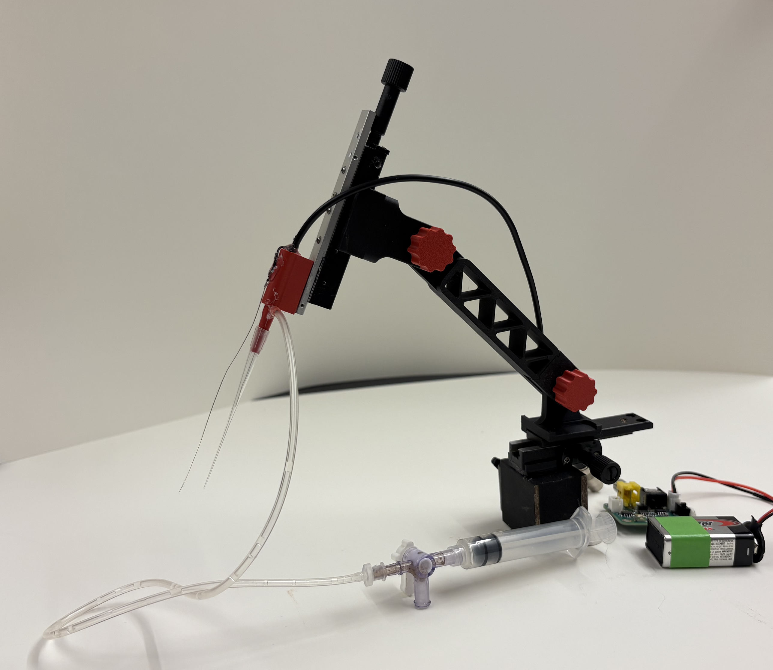
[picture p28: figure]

Designed by Dr. James Ryan for the CrawFly Collective

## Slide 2

Step 1: 3D print the parts for the boom arm

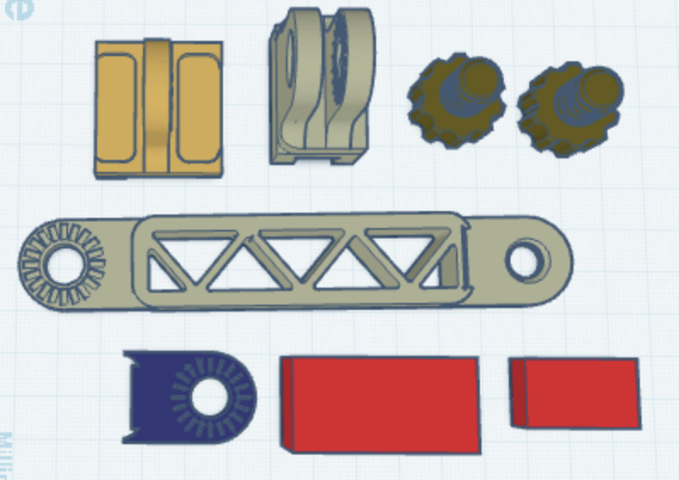
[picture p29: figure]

- Parts A, B, C must be printed with supports
- Parts should be printed with at least 50% infill for strength and rigidity
- The two screws (F) should be printed at 100% infill.

F

F

A

B

C

.stl files for the parts are available on our GitHib at:
https:// (https://github.com/CrawFly/DIY-Neuroscience)github.com (https://github.com/CrawFly/DIY-Neuroscience)/ (https://github.com/CrawFly/DIY-Neuroscience)CrawFly (https://github.com/CrawFly/DIY-Neuroscience)/DIY-Neuroscience (https://github.com/CrawFly/DIY-Neuroscience)

E

G

D

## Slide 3

Step 2: Prepare the base.

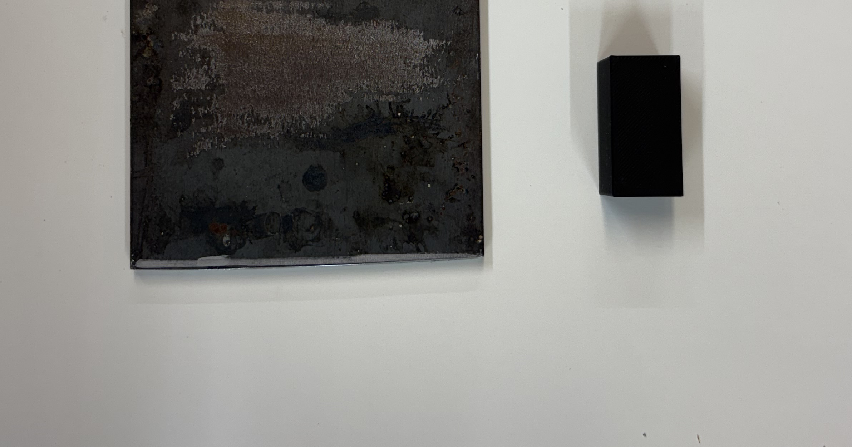
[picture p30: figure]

There are two options for bases:
1) A 4x4 inch sheet of 1/8th or ¼ inch steel plate. Available at Lowes or Home Depot
2) An On-Off magnetic base (used if you have a steel table).

Can be purchased from Harbor Freight for ~$13.00 US

1

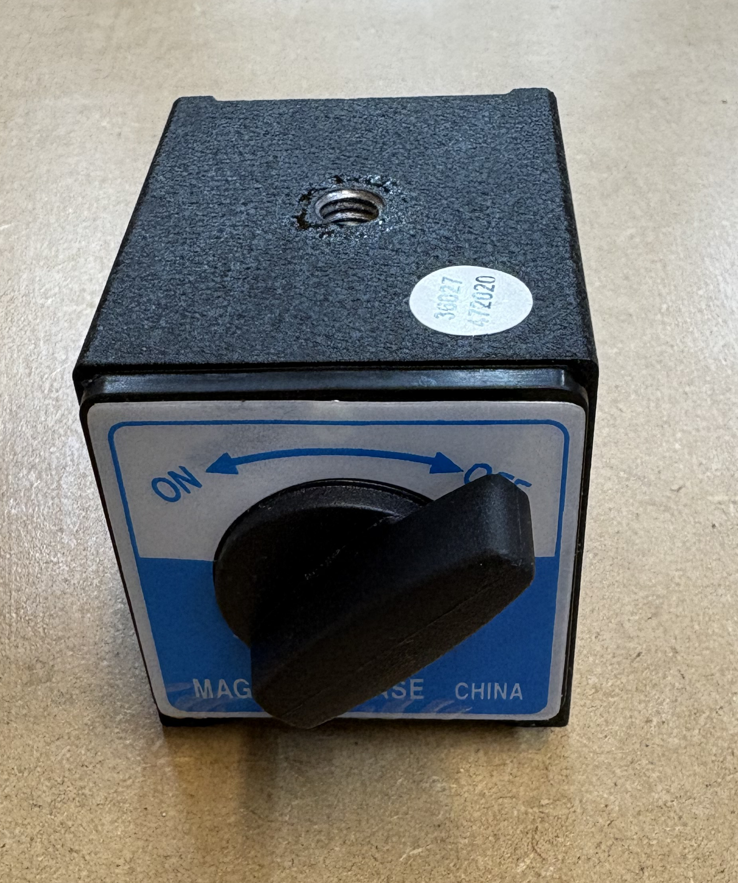
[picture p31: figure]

2

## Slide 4

Step 3: Superglue 3d printed part E to the center of either the steel plate or the top of the magnetic base.

Step 4: Prepare the two x-y microscope stages

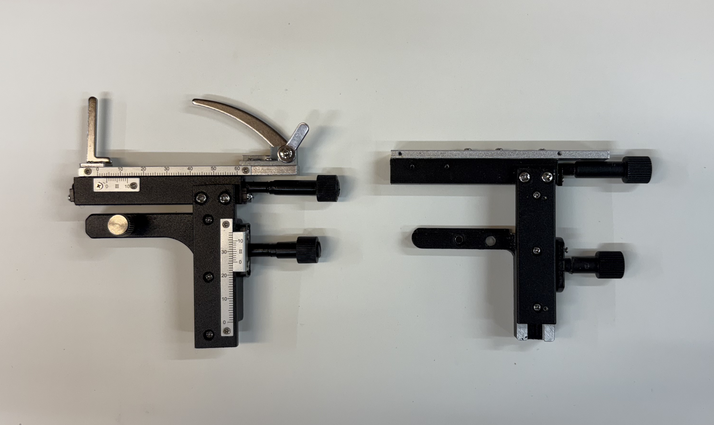
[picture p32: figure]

Begin by removing the slide holders from the top and the scales from the top and bottom sections as shown on the right

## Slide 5

Step 5: Remove the x axis from the y axis by removing the two sliver screws

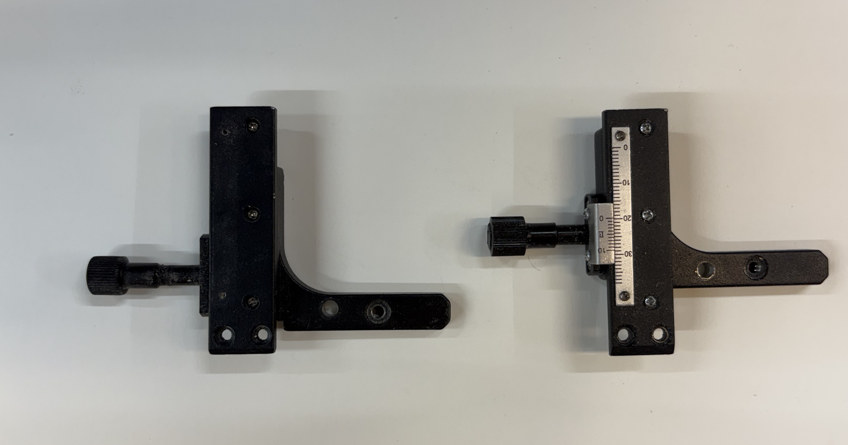
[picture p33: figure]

At this point you should have 2 x-axis parts that look like the one on the right in this photo.
You should also have 2 of the y-axis components (used later).

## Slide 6

Step 6: Using a hacksaw or band saw, cut the left side of the x-axis off as shown in the photo.

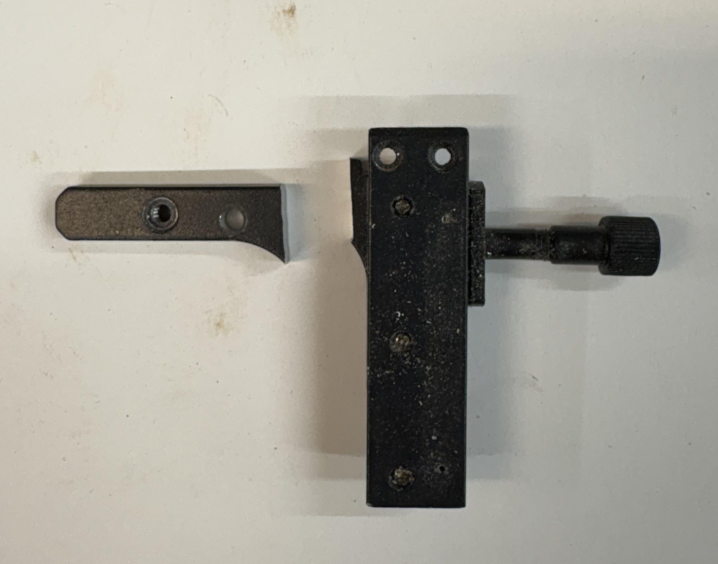
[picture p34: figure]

Repeat this process for both x-axis components

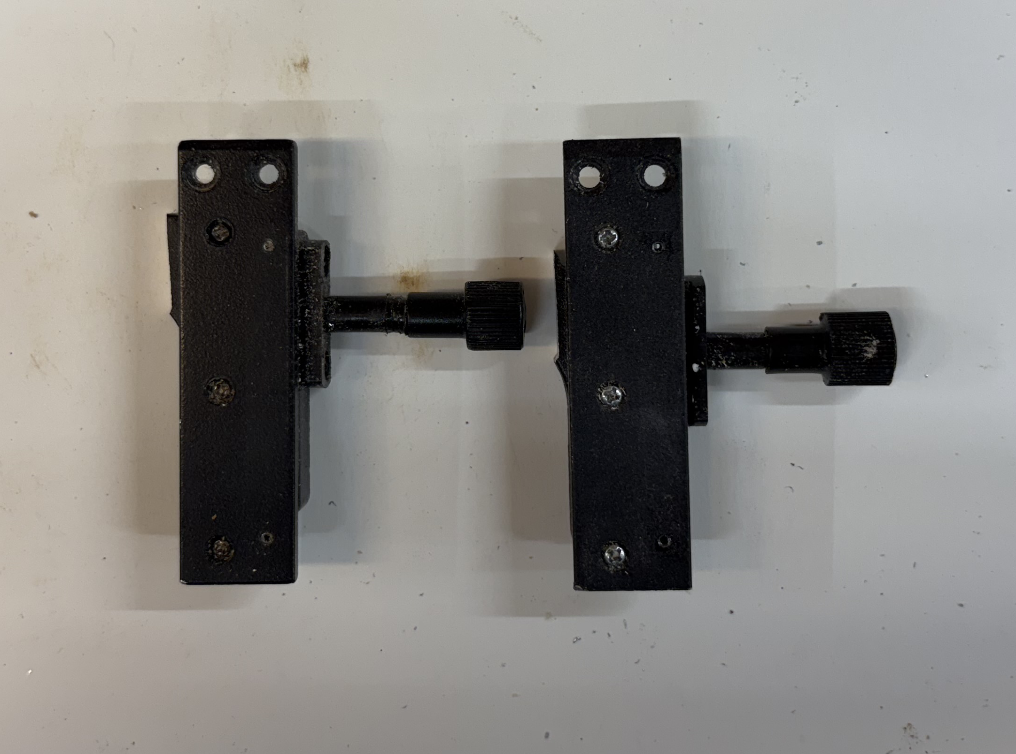
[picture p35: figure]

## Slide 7

Step 7: Use superglue or epoxy to glue 3D printed part E to the center of the base (either the metal plate or the magnetic base).

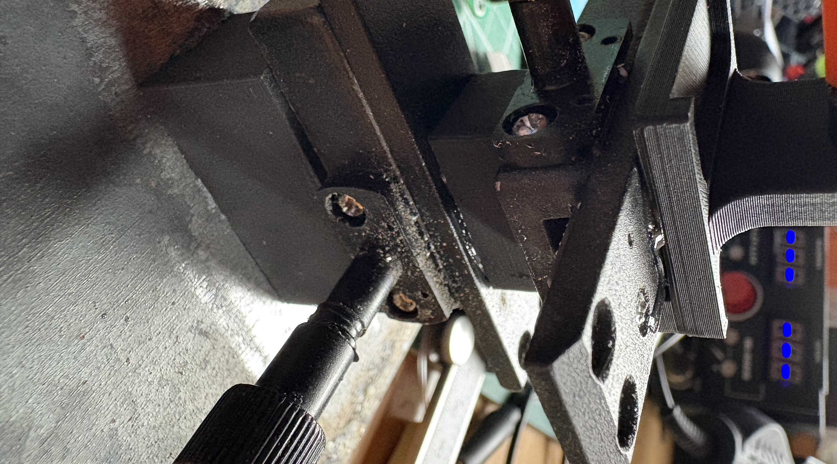
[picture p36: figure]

Step 8: Glue X-axis 1 to the top of block E keeping it in line with the long axis of block E
Step 9: Glue part G to the top of one of the x-axis components. It should be in line with the x-axis component. Be sure not to get glue into the moveable parts of the x-axis.

Step 10: Glue x-axis 2 to part G so that the thumb screws are 90 degrees to x-axis 1 (see photo).

X-axis 2

G

X-axis 1

E

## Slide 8

Step 10: Glue 3D printed part A on top of x-axis 2. The center post with the hole should be in line with the x-axis component

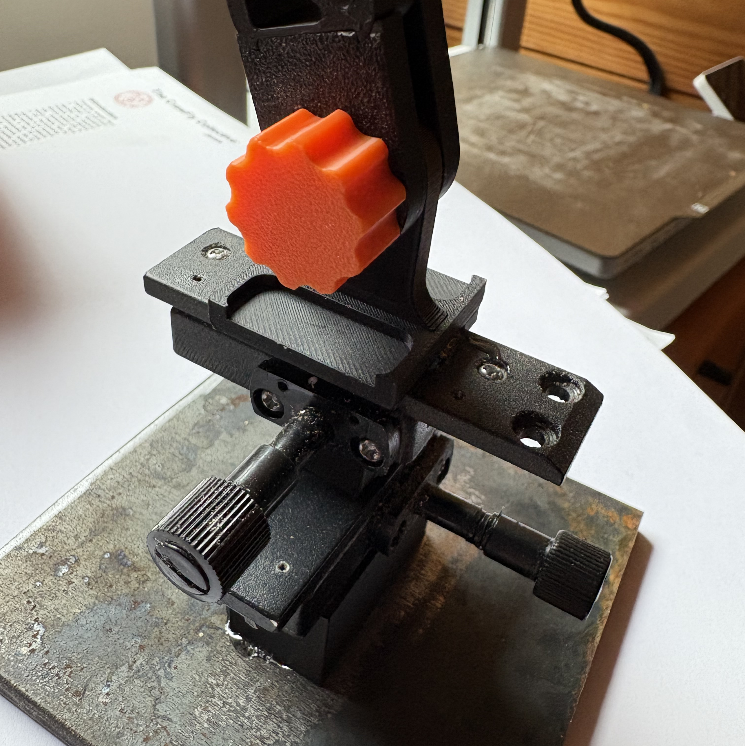
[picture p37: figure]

Part A

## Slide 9

Step 11: Prepare 3D printed parts C, D, and F as shown below on the left. Place parts C and D over the upright section of part A and thread the screw through the holes. Make sure part D locks into the boom arm and that the rough side of part D is against the rough side of part A.

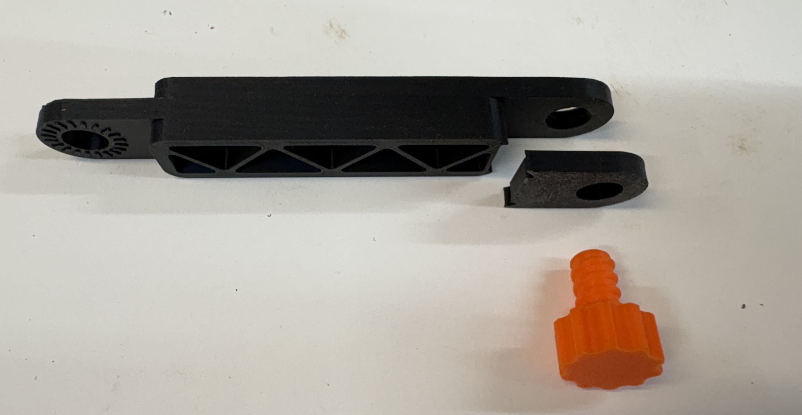
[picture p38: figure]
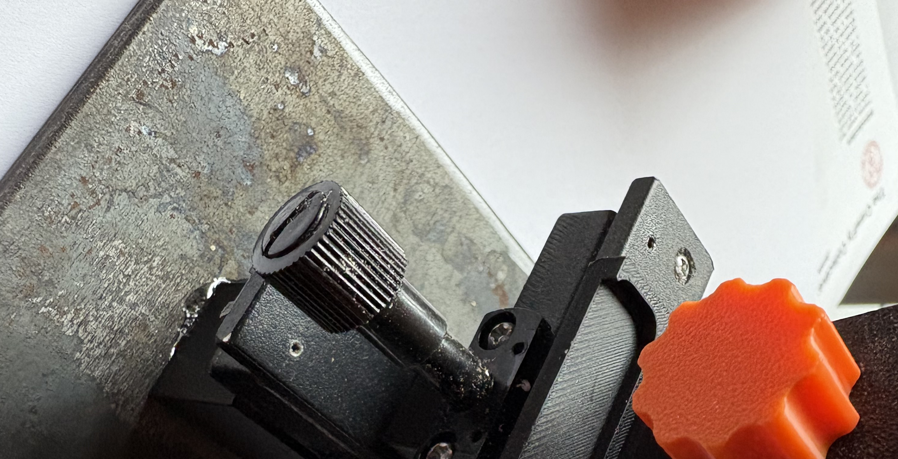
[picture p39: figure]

C

D

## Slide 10

Step 12: Slide 3D printed part B over the end of the boom arm (part C) and thread the second screw (F) through the holes.

Step 13: Glue one of the y-axis components into the slot in part B. Be careful not to get glue into the mechanism

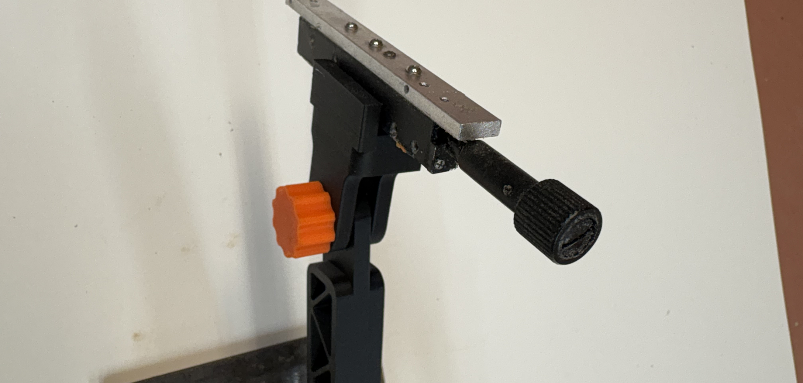
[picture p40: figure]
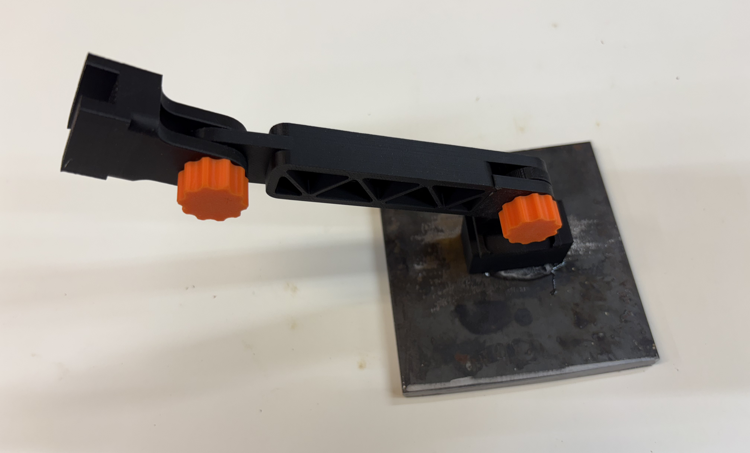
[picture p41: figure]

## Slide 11

Assemble the Wire Electrode

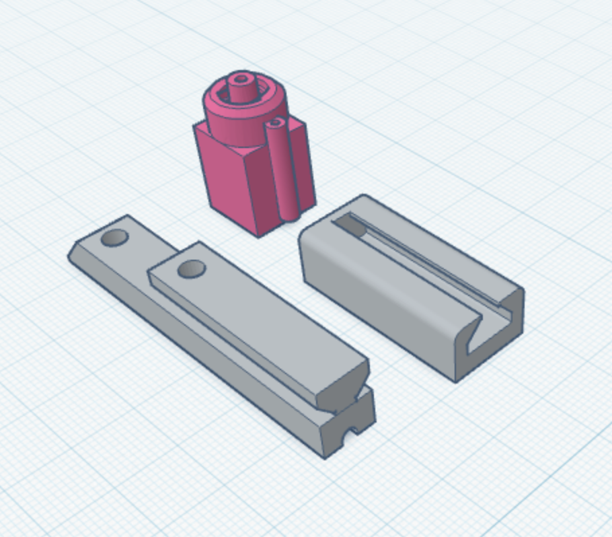
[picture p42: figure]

Step 14: Glue Part A to the top of the silver x-axis from Step 13. Make sure the slot in part A faces up.

C

Step 15: Slide the triangular dovetail from part B into the slot in part A

Step 16: Glue part C to the upper end of part B with the luer lock facing away from part A.

B

A

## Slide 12

Step 17: Insert the dispensing syringe needle into the luer lock from step 16.
Step 18: Use fine sandpaper to remove the coating from one end of the coated copper wire.
Step 19: Carefully insert a 5-6 inch piece of coated copper wire into the metal needle until it sticks out the back of the electrode holder part C
Step 20: Solder the newly sanded end of the electrode wire to the red wire of the audio jack and secure the wires to the plastic holder with glue or blue dental wax.
Step 21: Solder a 5-6 inch piece of bare copper wire to the end of the black wire on the audio jack and cut off the white wire (it is not used). Slide the bare wire through the small tube (or into the small groove) on the outside of the plastic electrode holder and secure it with glue. This will serve as the reference electrode.

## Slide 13

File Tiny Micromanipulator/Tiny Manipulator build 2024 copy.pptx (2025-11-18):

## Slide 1

DIY – Building the “Tiny” micromanipulator

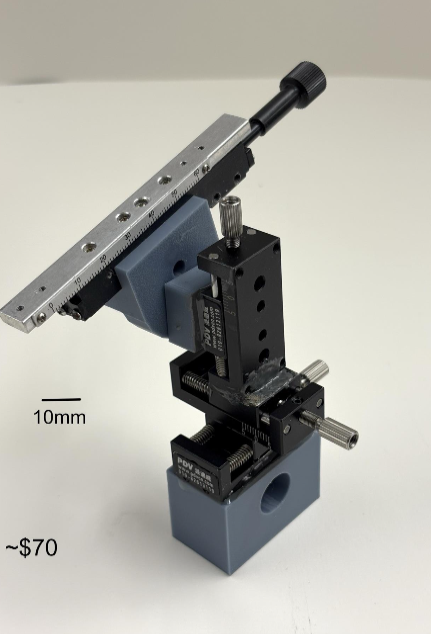
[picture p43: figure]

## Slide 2

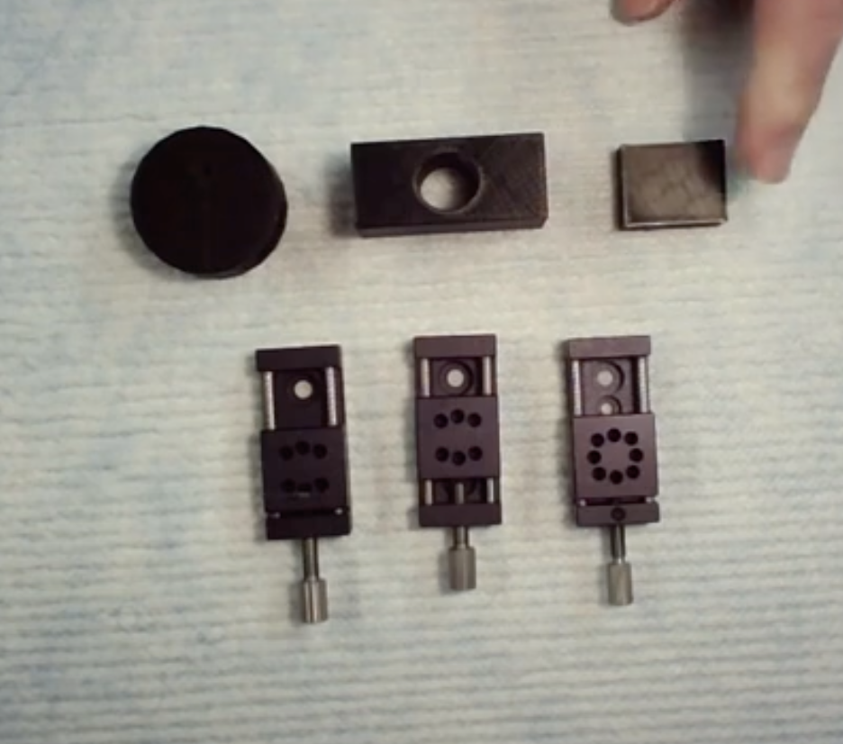
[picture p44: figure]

The Parts

3 - 3D printed parts
-print at 80% infill

3 small linear stages

https://www.alibaba.com/product-detail/PT-SD10-Miniature-Manual-Linear-Stage_60537789251.html

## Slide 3

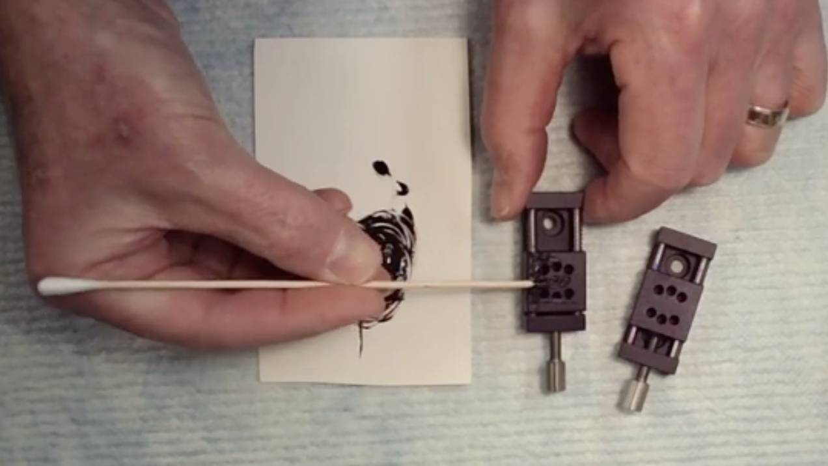
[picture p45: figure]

4) Butter epoxy onto the small top plate of one stage.
- do not get much epoxy into the six little holes

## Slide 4

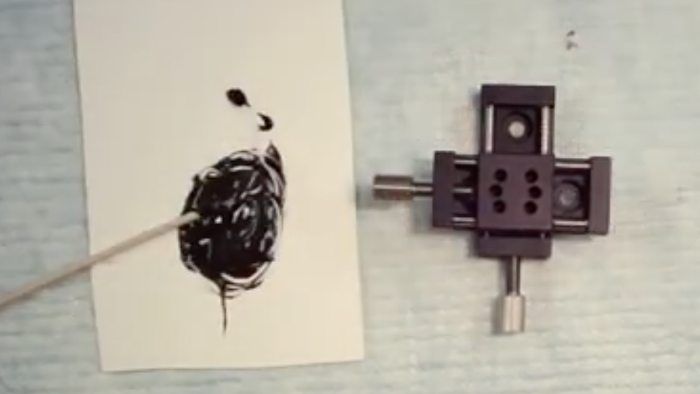
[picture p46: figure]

5) Place a second linear stage onto the small top plate of the stage you just buttered
ORIENTED 90 DEGREES TO LOWER STAGE

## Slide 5

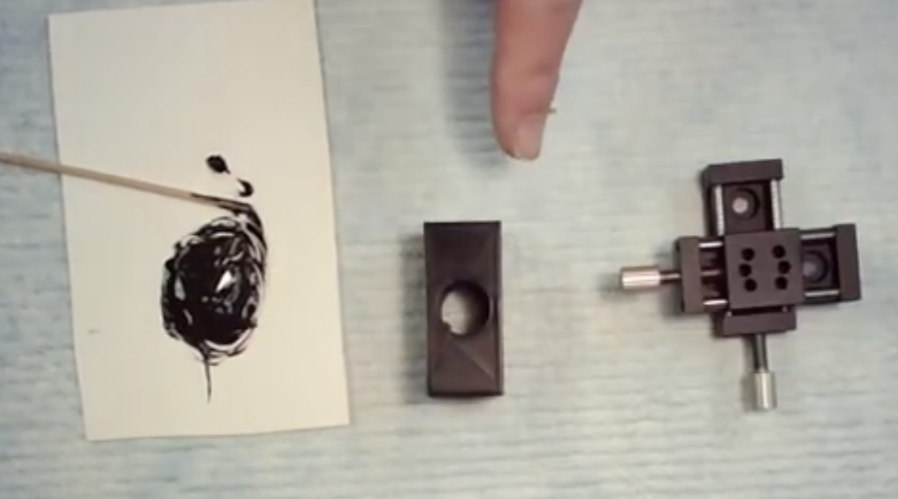
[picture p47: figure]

1) Mix 2 part, 5-min epoxy

2) Butter epoxy onto non-hole side of 3D printed base
see blue arrow

3) Place bottom of one linear stage onto epoxy

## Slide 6

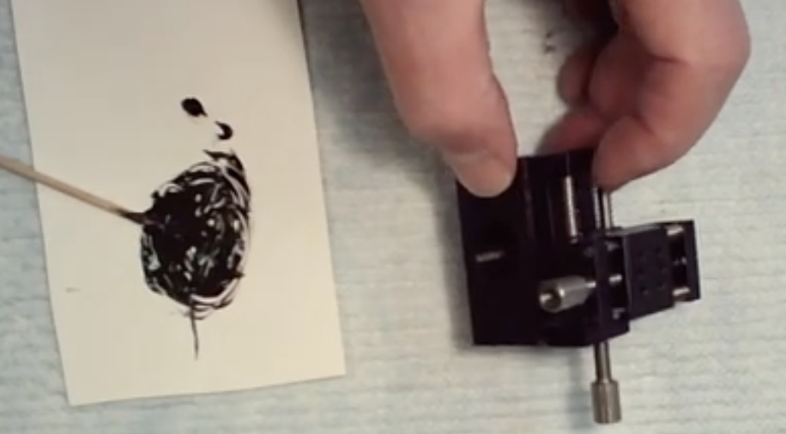
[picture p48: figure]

It should now look like this – PUT ASIDE AND LET EPOXY DRY

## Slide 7

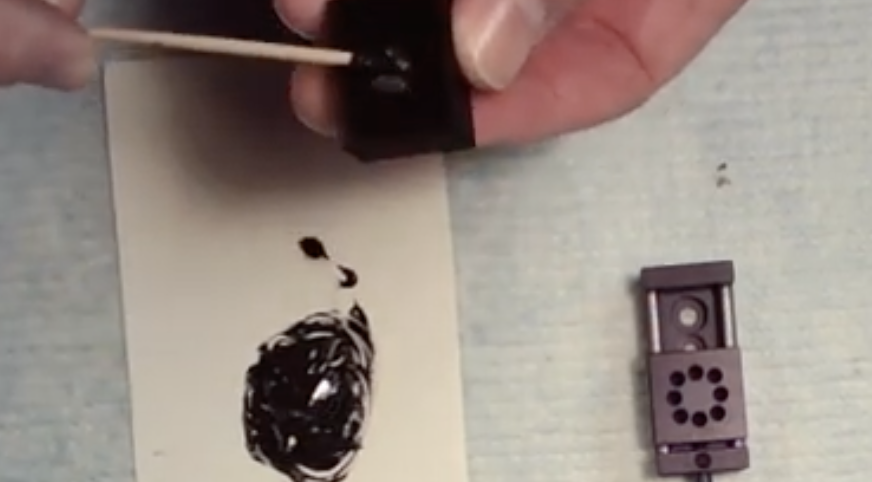
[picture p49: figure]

7) Butter epoxy on the back of the small 3D printed square.

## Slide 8

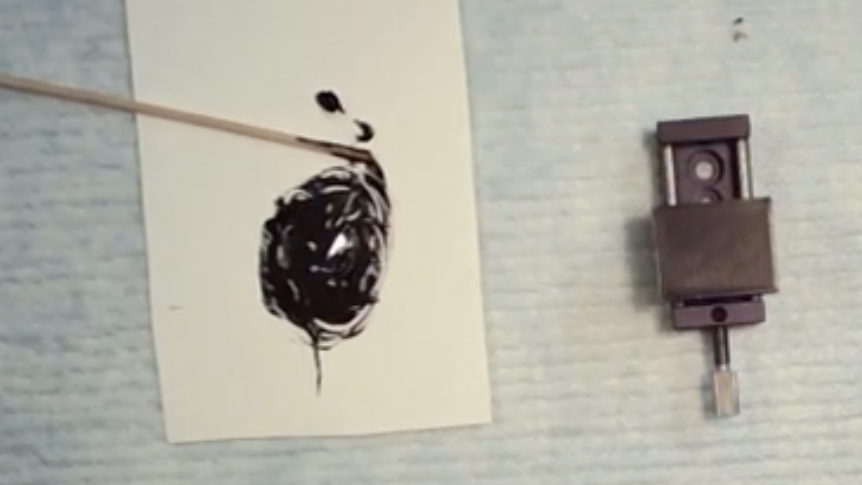
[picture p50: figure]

8). Place the epoxy side of the square down onto the third moveable square of the linear stage as shown below. Try not to get lots of epoxy into the six holes on the stage.

Set aside to dry

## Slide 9

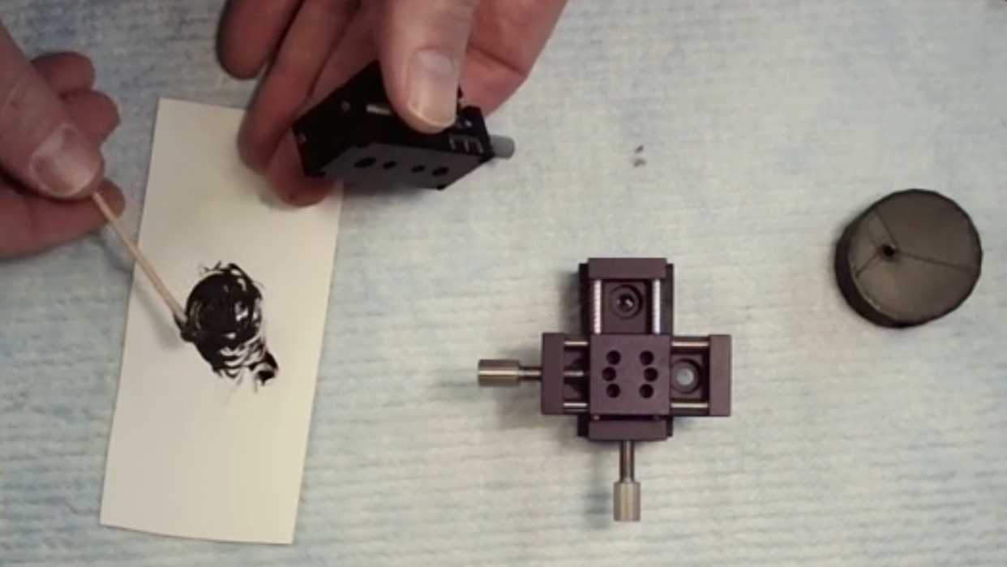
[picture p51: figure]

9) When all parts are cured (~ 15-20 minutes for 5-minute epoxy) butter fresh epoxy onto the END of the stage with the square 3D printed part (blue arrow) – and place it vertically onto the x-y stage (red arrow).

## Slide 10

You should now have a 3-axis manipulator

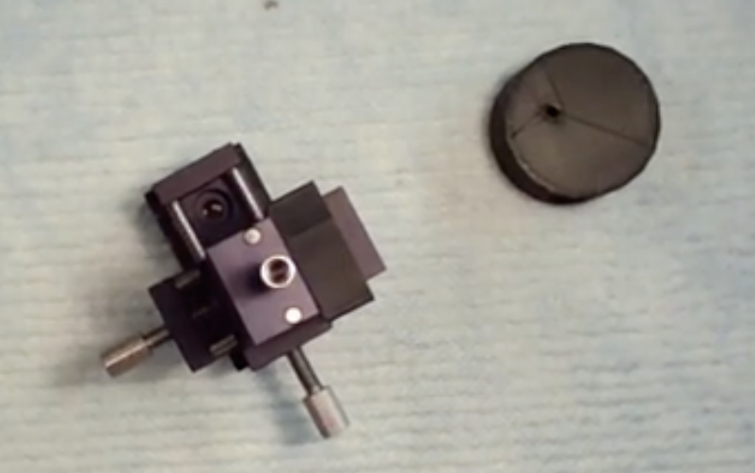
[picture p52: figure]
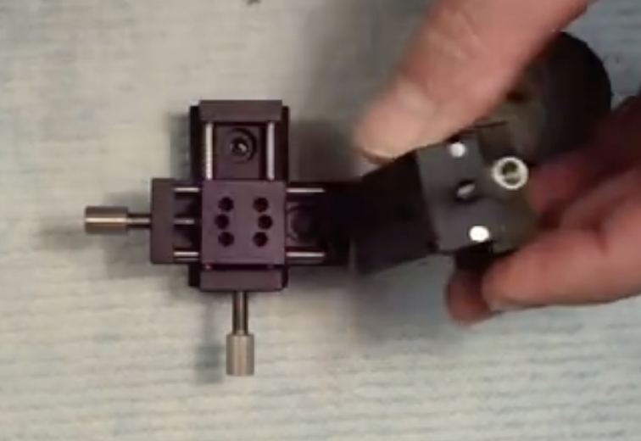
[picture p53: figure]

Let it dry fully

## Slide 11

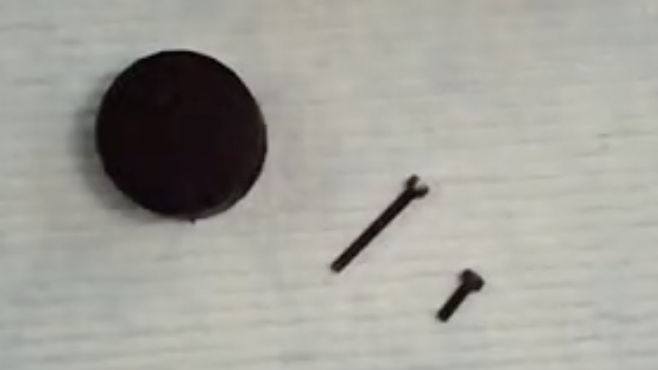
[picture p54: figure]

10) The circular 3D printed part is the Probe Holder. There are 2 screws needed to mount the holder to the 3-axis manipulator.

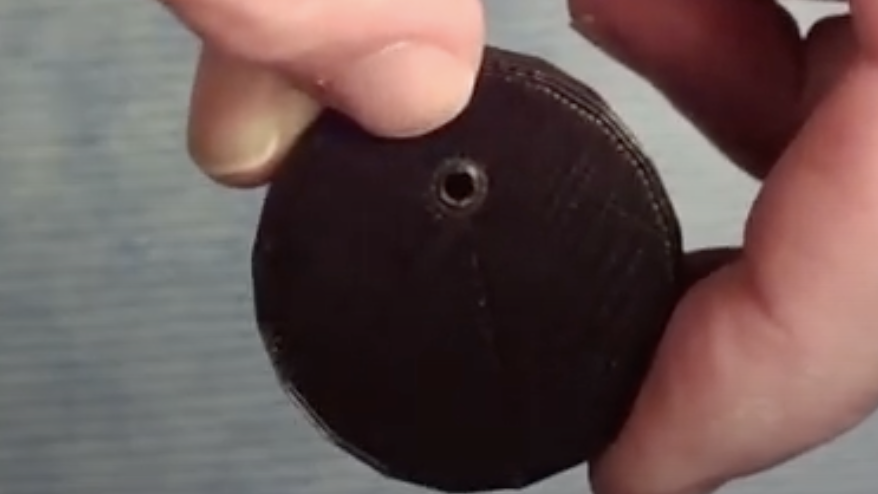
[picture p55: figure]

11) The long screw gets threaded onto the small 3mm hole in the side of the probe holder - arrow

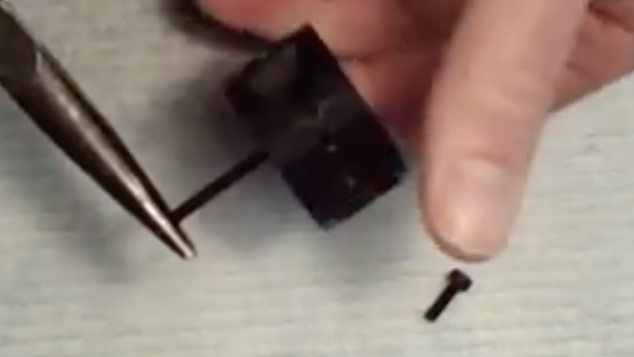
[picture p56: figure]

12) Screw in the screw until it just protrudes from the other side

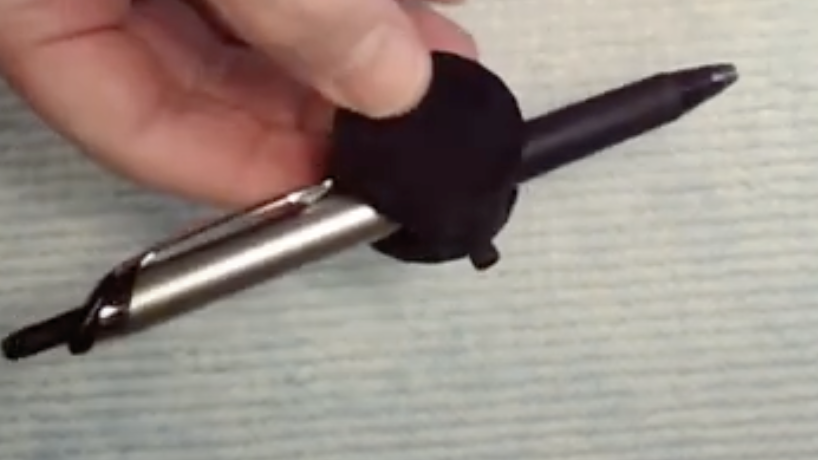
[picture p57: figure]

13) Screw in the smaller screw that will hold the probe into the side of the circular part as shown above

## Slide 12

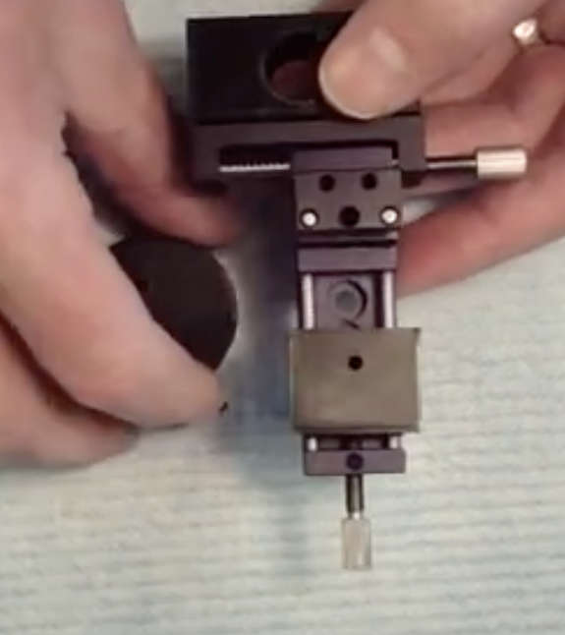
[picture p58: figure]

14. Finish mounting the probe holder to the 3-axis stage by further screwing in the long screw into the hole on the square 3D printed part - arrow

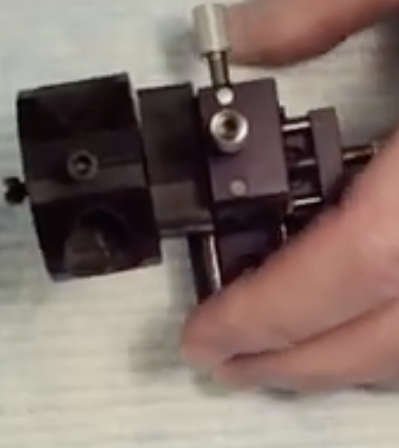
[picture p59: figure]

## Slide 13

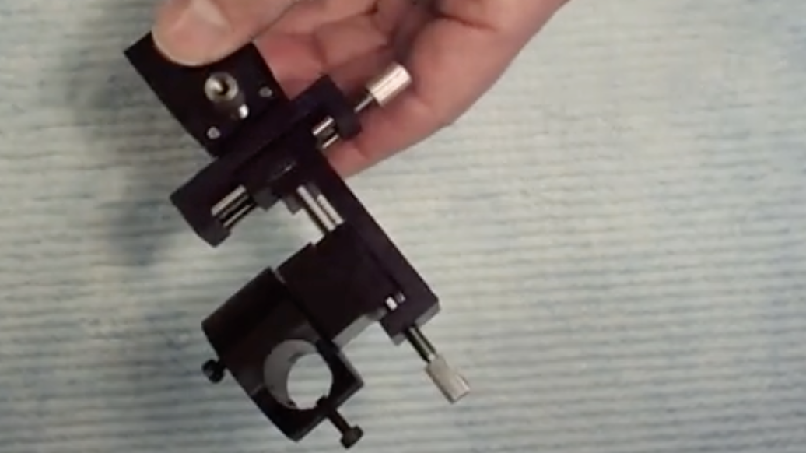
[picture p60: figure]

Finished 3-axis manipulator

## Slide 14

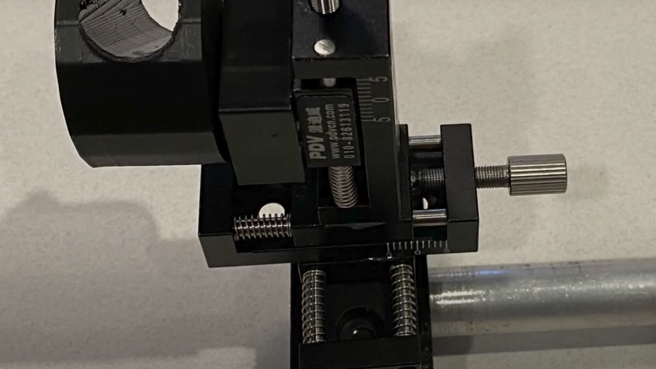
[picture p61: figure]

Optional – epoxy the ½ inch diameter rod into the hole in the base

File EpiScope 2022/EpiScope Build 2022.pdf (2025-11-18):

# Building the EpiScope

## Parts Needed: Mechanical Parts

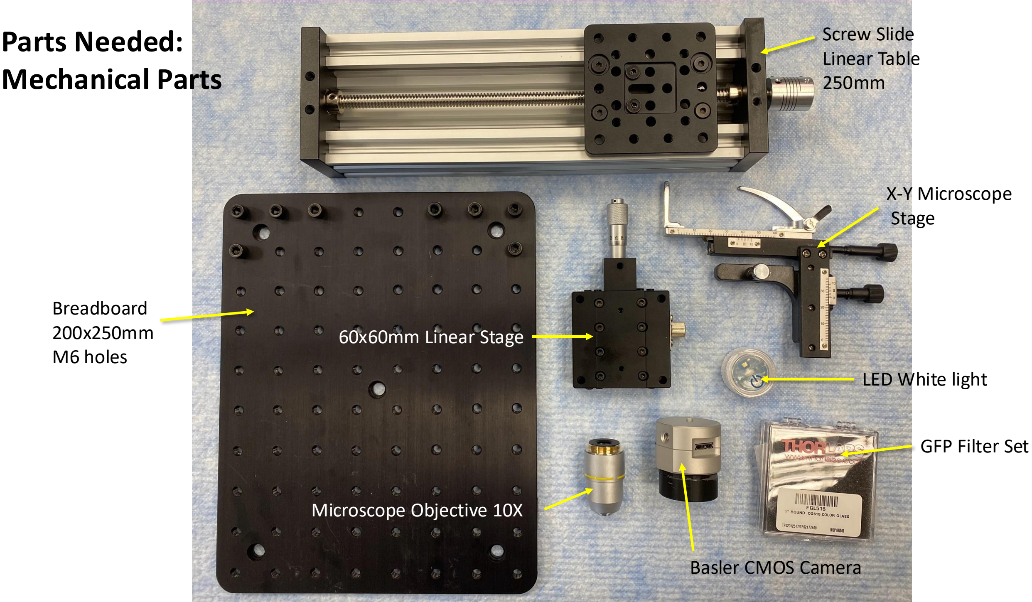
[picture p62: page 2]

Screw Slide
Linear Table
250mm

X-Y Microscope
Stage

GFP Filter Set

LED White light

Basler CMOS Camera

Microscope Objective 10X

60x60mm Linear Stage

Breadboard
200x250mm
M6 holes

## Tools Needed:

Drill and Drill Bits
(optional)

### 2 Part Epoxy

Small Phillips
Screw drivers
Hex head
Drivers -Metric

## EpiScope 3D Printed Parts

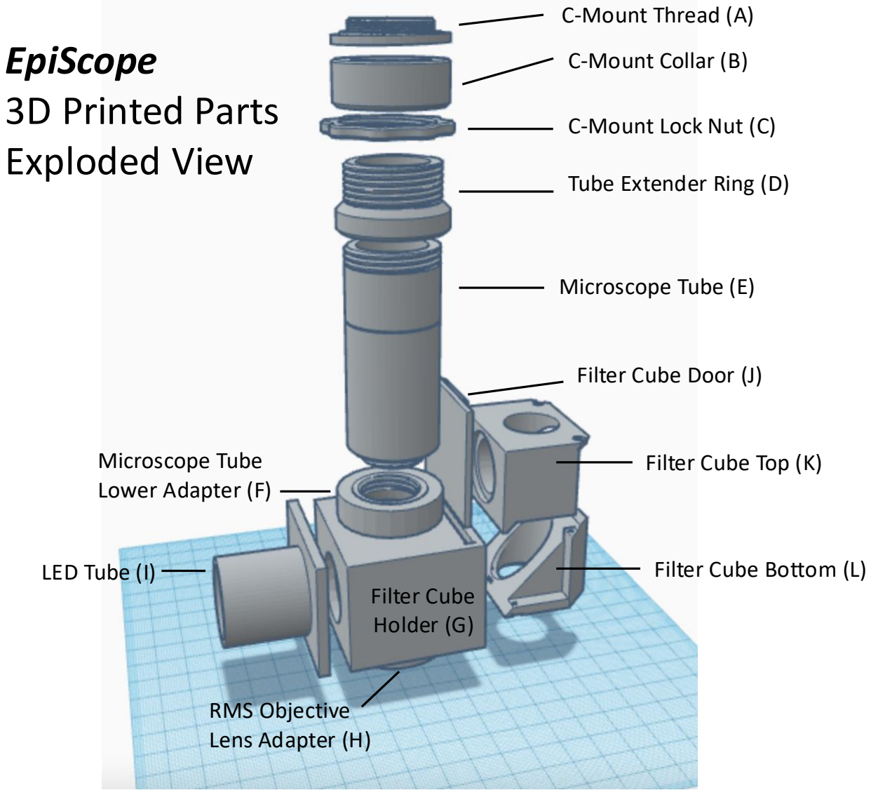
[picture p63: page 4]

C-Mount Thread (A)

C-Mount Collar (B)

C-Mount Lock Nut (C)

Tube Extender Ring (D)

Microscope Tube (E)

Filter Cube Door (J)

Filter Cube Top (K)

Filter Cube Bottom (L)

Microscope Tube
Lower Adapter (F)

LED Tube (I)
Filter Cube
Holder (G)

RMS Objective
Lens Adapter (H)

## Exploded View

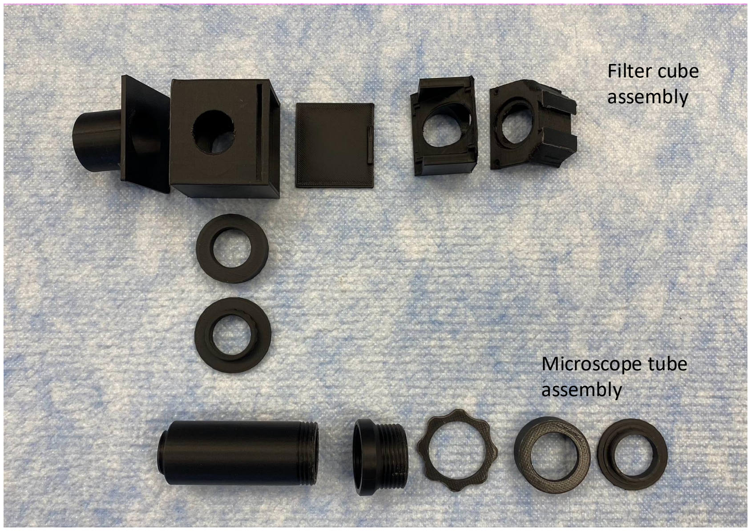
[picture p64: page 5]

3D Printed Microscope Parts

Filter cube
assembly

Microscope tube
assembly

## 3D Printed Mounts and Stage Assembly

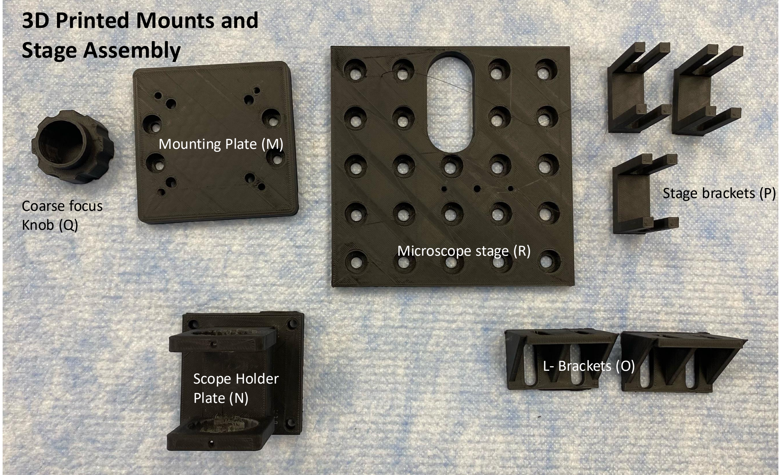
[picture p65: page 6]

Microscope stage (R)

Mounting Plate (M)

Scope Holder
Plate (N)

L- Brackets (O)

Stage brackets (P)
Coarse focus
Knob (Q)

## Step 1: Epoxy parts A and B together (part A sits onto of part B)

(B) (A)

## Step 2: Epoxy scope tube lower adapter (F) to top of filter cube holder (G)

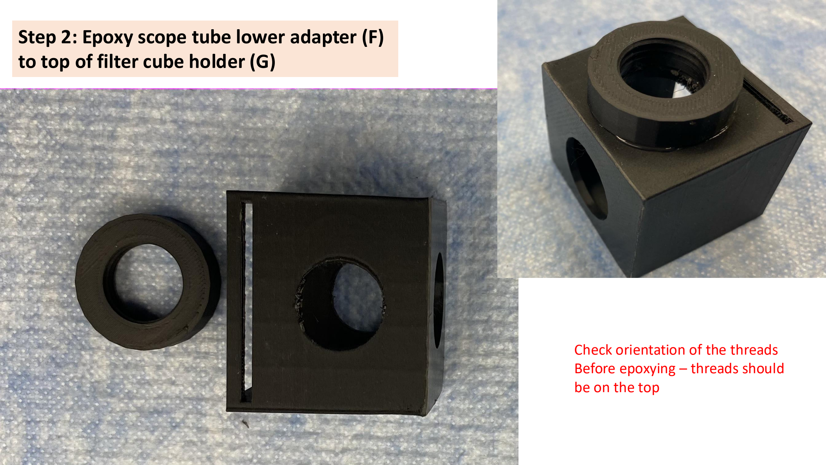
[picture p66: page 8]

Check orientation of the threads Before epoxying – threads should be on the top

## Step 3: Epoxy the LED tube (I) to the filter cube holder (G)

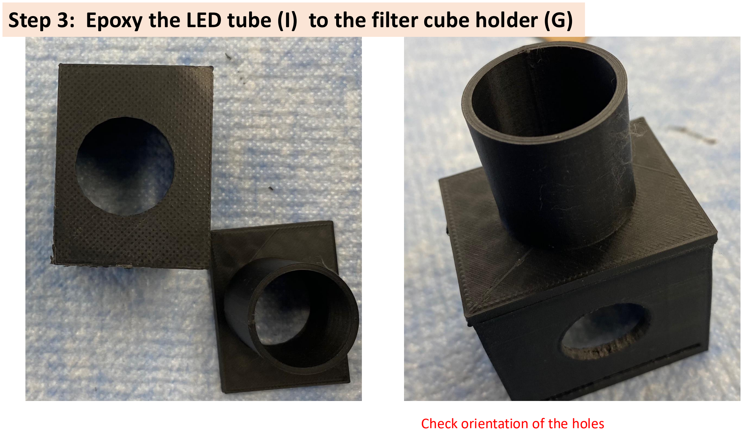
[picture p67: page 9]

Check orientation of the holes

## Step 4: Epoxy RMS objective lens adapter (H) to the bottom of the


## filter cube holder (G)

(H)

(G)


Step 5: Attach the Mounting plate (M) to the linear stage plate using 4 M5x 8mm pan head screws

(M)

Note the orientation of
the holes on plate M

(M)

M5x8mm Pan head screws


Step 6: Attach the 60x60mm x-axis linear stage to the mounting plate (M) using 4 M4x8mm hex-head screws

M4 screws


Step 7: Attach the microscope tube
(E) to the scope holder plate (N) by sliding it through the openings. Secure with M3 screw. Attach the scope tube assembly to the x-axis liner stage with 4 M4x10mm pan head screws

M3 screw

M4x10 screws


Step 8: Thread the tube extender ring (D) onto the top of the microscope tube (E). Thread the C-mount lock-nut (C) onto the tube extender ring (D).
Thread the C-mount collar assembly (A and B) onto the tube extender ring (D)
(E) | (D) | (C) | (A&B)


Step 9: Mount the entire scope assembly onto the optical base plate using the 2 narrow angle brackets. First thread M5x8mm screws through the longer opening and loosely attach an M5 t-slot nut.
Then drop the nuts into the channels on the Linear stage and finger tighten.

M5 T-nuts

Step 10: Adjust the fit of the two screws on the vertical column and and add 2 M6x8mm screws to attach the vertical column to the horizonal base plate.

M5 screws

M6 screws


Step 11: Thread the filter cube holder assembly (parts G, I, F, and H epoxied together) onto the bottom of the microscope tube (E)

LED tube should face to the side

(E)

(G,I,F,H)


Step 12: Mount the microscope stage to the base plate using 3 stage brackets (P) and M5x10mm screws with nuts through the top and M6x8mm screws to hold the brackets to the base plate. Make sure the large opening on the stage is centered under the objective lens.


Step 13: Attach the x-y microscope stage to the top of the stage plate by inserting the pins on the x-x stage into the holes on the 3D printed stage plate. You can epoxy it in place if you want added stability.

X-Y stage

Stage Plate (R)


Step 14: Attach the coarse focus knob (Q) to the top of the linear screw stage (vertical column) and tighten with a M3 screw.

(Q)


Step 15: Screw an objective lens (10X) into the RMS objective lens adapter (H)


Step 16: Prepare the filter cube

Filter cube top (K)
Filter cube bottom (L)

GFP filter set

White cotton gloves
Double-sided tape

Tiny screws or double-sided tape

K

L


Place two small strips of double-sided tape on either side of the cube (K) to to
hold the mirror in place

Wearing white cotton gloves – carefully place the dichroic mirror on the 45-degree platform in the bottom filter cube (L)

Follow manufacturers instructions for positioning the filters


Place filter cube parts together and screw in two mini screws to secure the top and bottom of the cube together

Place two small strips of double-sided tape onto the lower rim of the filter opening and gently insert the glass filter.

Follow manufacturers instructions for correct orientation of the filters.

Tape

Repeat the process for the remaining filter.

Slide the completed filter cube into the filter cube holder (G) with the dovetail facing away from the LED source.

G


Slide the filter cube in all the way. Insert the filter cube door
(J) into the slot on the top of the filter cube holder (G)

(J)
G


Step 17: Attach the camera to the C-Mount

Here a color HDMI camera has been attached


Step 18: Inserting the LED light

LED

## Building the LED light source

Qt | Part | Unit cost | Total cost | Source
1 | Lueon rebel 470nm Blue LED w/ 9o optic 700mA | $ 7.33 | $ 7.33 | https://www.ledsupply.com/leds/luxeon-rebel-color-leds
1 | Carclo lens -frosted narrow spot | $ 1.25 | $ 1.25 | https://www.ledsupply.com/led-optics/10194-carclo-lens-frosted-narrow-spot-led-optic
1 | heat sink 1 up LED Housing | $ 10.99 | $ 10.99 | https://www.ledsupply.com/led-heatsinks/dynamic-led-heatsink-housing
1 | wire harness for BuckPuck | $ 4.99 | $ 4.99 | https://www.luxeonstar.com/wiring-harness-for-buckpuck-drivers-6-wire-with-pot
1 | Dimmable BuckPuck 1000mA | $ 14.99 | $ 14.99 | https://www.luxeonstar.com/1000ma-externally-dimmable-buckpuck-dc-driver
1 | Project box (or equivalent) | $ 4.41 | $ 4.41 | https://www.amazon.com/BUD-Industries-CU-1874-B-Plastic-Utility/dp/B005T5CZHC/ref=sr_1_55?fst=as%3Aoff&qid=1572178033&refinements=p_n_feature_keywords_browse-bin%3A2803809011%2Cp_36%3A1253528011&rnid=1243644011&s=hi&sr=1-55
1 | 12V Power Supply (12V-5Amp AC/DC adapter | $12 | $12 | Any source

Bill of Materials


LED Wiring Diagram

To 12V wall
adapter

Pick appropriate color LED for your fluorescence probe

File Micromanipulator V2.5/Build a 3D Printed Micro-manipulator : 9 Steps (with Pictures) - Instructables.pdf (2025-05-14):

## Build a 3D Printed Micro-manipulator

By Remi_Rafael (https://www.instructables.com/member/Remi_Rafael/) in Workshop (https://www.instructables.com/workshop/)Science (https://www.instructables.com/workshop/science/projects/)

## Introduction: Build a 3D Printed Micro-manipulator

Micromanipulators are tools designed to precisely handle objects at the micron scale. They are very important in science as they allow to interact directly with microscopic device, when direct manual handling would most likely result in destruction. However, professional quality micromanipulator can be very expensive (thousands of USD), out of reach of hobbyists and sometimes a scarce resource even for professional researchers.

Some models of 3D printed micromanipulators exist and have been published in open source, but the ones I tried previously suffered from backlash and ratcheted movements due to the sliding of plastic on plastic. In this design, I have tried to remedy these issues by loading all axes with springs and by using metallic rods to prevent any plastic-plastic contact. All sliding surface are metal against printed plastic. The result is a stiff, compact and smoothly moving micromanipulator, not quite up to par with the commercial alternatives, but fit for most applications and accessible for a handful of USD and half an hour of your time.

I have also designed a series of linear and rotational stages for (inexpensive) precision positioning. If interested you may find more information on my other instructables here, (https://www.instructables.com/Build-a-3D-Printed-Linear-Stage/) and here. (https://www.instructables.com/Build-a-3D-Printed-Rotational-Platform/)

## Supplies

Materials:

1. 2x 55mm and 1x 50 mm M3 bolt
2. 3x M3 nuts and washer
3. 3x 40mm springs (40/50 min/max length, 7.5 max outer diameter, 3.5 min inner diameter, 0.6 to 0.8 recommended wire diameter)
4. 4x 52.5, 4x 63.5 and 3x 44.5 mm long 2 mm diameter metallic rod
5. 8x 12mm diameter 3mm thick magnet (other dimensions are possible if preferred, see 3D files description)
6. 4x M3 4mm diameter 4mm long melt inserts (other dimensions are possible if preferred, see 3D files description)

Optional (tool holder head)

1. 4x 8mm M3 screws
2. (straight holder tool) 3x M3 insert 1x 20mm and 2x 14mm M3 screw 1x M3 washer
3. (bended holder tool) 2x M3 insert 2x 14mm M3 screw

3D printed parts:

1. 1x Base
2. 1x Middle
3. 1x Top
4. 1x Z slider
5. 3x Knob
6. 1x Tip holder (depending on your preference)

Tools

1. 3D printer with PLA filament
2. Vice
3. Metal saw
4. File
5. 1.9 or 1.95mm drill bit (slightly undersized compared to your metal rod is preferred)
6. Electric drill/Screw driver
7. Supports removal tools (cutter, pliers...)
8. Melt insert installation tool, or soldering iron (,or lighter if you like it ghetto style)
9. (optional) grease or oil lubricant
10. (optional) glue

## Step 1: Print the Parts and Prepare Yourself

Before starting, one word on the design strategy: FDM 3D printing is not precise enough to make rigid printed parts assemble perfectly together without any play (at least not with someone else's printer ^^). This is a huge issue to build a micromanipulator since even a small play can ruin your precision. To go around this difficulty, all the printed parts are designed to be slightly tight and need to be adjusted. However we can use the low transition temperature of PLA to easily achieve a very tight fit. All the parts are connected via metal rods. By spinning these rods very fast with a hand-drill in there assembled position, the friction will heat the rod and the plastic locally where the fit is tightest. As soon as the rod reaches about 70°C, the PLA will start to deform and you will get a perfectly sized hole.

This method is quite efficient but it requires some patience and method. Be cautious not to overheat your parts or you will need to re-print it... Always place all the other rod guides when doing it, to ensure that the two parts are maintained in the right position. Use this method every-time the fit is too tight and the parts do not slide well enough.

The standard files are designed for a printer with a clearance of 0.2mm. If your printer requires a larger clearance it means you will need to take a little more time with the drill, or you can look for "large clearance" files (I plan to add those soon after this tutorial is released). If you don't know the adequate clearance for your printer, you can look at the test part included. I also included various versions of the printing files depending on the type of magnets or melt inserts you have available. Some parts require supports and the printing orientation will influence the final result so make sure to read the description.

Based on those considerations you should look into the files available in the following links and print the most appropriate for you:

https://www.printables.com/model/895311-3-axis-micromanipulator

## Step 2: Source Your Materials

I tried to design this project with standard, easy to procure materials but that doesn't guarantee you will have them on stock. Here are some links to help you gather what you need. For each one, I've tried to include one link from Taobao (Chinese platform) and one from Amazon. I nevertheless would like to encourage you to find local providers and limit oversee delivery whenever possible...

2x 55mm and 1x 50 mm M3 bolt (2x 60 and 1x 50 would also work, you can off course buy only 55mm and cut one to size) I use mostly internal hex bolts but any kind of head type is ok if you are ready to grind the head perimeter a little.

amazon, (https://www.amazon.com/M3-0-5-Socket-Screws-Machine-Thread%EF%BC%8CHalf/dp/B08X3QKDMK) taobao (https://detail.tmall.com/item.htm?_u=q209fqk4rg63ac&id=730911551951&spm=a1z09.2.0.0.72542e8dkL4PFf)

3x M3 nuts and washers

amazon, (https://www.amazon.com/Uxcell-a16033100ux0563-Carbon-Steel-Hexagon/dp/B01IWUSDYY) taobao (https://item.taobao.com/item.htm?ali_trackid=1_e0fc3a62324d0f807a836a351999d875&id=604071198617&skuId=4228430180700)amazon, (https://www.amazon.com/Washer-Stainless-Steel-Washers-100PCS/dp/B0BGH5Y5LQ) taobao (https://detail.tmall.com/item.htm?ali_trackid=1_02a48190d072578e09c77f7f601b1761&id=40187996496) (only follow these links if really necessary, you most likely don't need 100...)

3x 40mm springs (40/50 min/max length, 7.5 max outer diameter, 3.5 min inner diameter, 0.6 to 0.8 recommended wire diameter)

amazon (https://www.amazon.com/Boxonly-Compression-Machinery-Industrial-Compressed/dp/B0CGHWP2Y5) or amazon, (https://www.amazon.com/Diameter-Stainless-Compression-Spring-Length/dp/B0B7DYBD94) taobao (https://detail.tmall.com/item.htm?_u=q209fqk4rgbabc&id=526164033275&spm=a1z09.2.0.0.72542e8dkL4PFf)

2 mm diameter metallic rod (stainless steel advised, at least 15mm if you want to limit the waste when cutting to size)

amazon, (https://www.amazon.com/uxcell-200mm-Stainless-Steel-Solid/dp/B082ZP75G9?th=1) taobao (https://item.taobao.com/item.htm?abbucket=9&id=673027390555&ns=1&skuId=4841847632338)

8x 12mm diameter 3mm thick magnet (other dimensions are possible if preferred, see 3D files description)

amazon, (https://www.amazon.com/Magnets-Refrigerator-Neodymium-Whiteboard-Kitchen/dp/B0CCVPVQ1L) taobao (https://item.taobao.com/item.htm?_u=q209fqk4rgd5ee&id=595666159763&spm=a1z09.2.0.0.72542e8dkL4PFf)

4x M3 4.2mm diameter 4mm long melt inserts (other dimensions are possible if preferred, see 3D files description)

amazon, (https://www.amazon.com/BAISULI-Printer-Injection-Molding-Embedded/dp/B0CXH9ST64) taobao (https://item.taobao.com/item.htm?_u=q209fqk4rgb22c&id=678253123283&spm=a1z09.2.0.0.72542e8dkL4PFf)

## Step 3: Cut the Rods to Length


For this assembly, you will need 2mm rods cut into 4x 52.5mm segments, 4x 63.5mm segments and 3x 44.5mm segments. You can of course cut them by hand, or you can choose to print and use the cutting guide I designed. The one shown in the illustration offers 6 different lengths adapted for this project and to my 3D printed linear axis. You can choose to print the smaller version with only the relevant lengths for the micromanipulator.

To cut the wire, first grind the extremity flat with the file (factory rods are often cut with pliers, causing an uneven top surface) and insert it into the guide. Cut the wire at the adequate length and grind the second end.

To facilitate the insertion, I advise to add a chamfer at one end. To do that, fix the rod in the drill and spin the tip against the file.

## Step 4: Install the Magnets and Assemble the Knobs


The first assembly step is the installation of the magnets. The standard base file is designed with 4x 12mm holes to place 2x 3mm thick magnets in each. By alternating the polarity of each magnet pair, you can slightly increase the holding force. It will also prevent the iron substrate from
becoming also magnetic and attracting everything around.

After that, you can install the knobs. They are designed to be tight so you can just fix them in a vice and screw the bolts inside. If it is too lose, add a drop of glue on the head.

## Step 5: Assemble the Y Axis


To assemble the Y axis, first insert a nut in the hexagonal hole of the "middle" part. It is designed to be tight and the nut should hold in place. If it is too tight to insert manually, you can place it on a bolt, heat it with a lighter and insert it hot. If it is too lose, you should glue it.

After that you can place the "middle" part into the "base" and insert the 4x 44.5mm rods chamfer first. If insertion is really too difficult, use a slightly undersized (1.9mm or so) drill bit to clean the holes until insertion becomes possible.

You can then test the movements of the two parts. At this point, the fit should be very tight and the parts should have a hard time moving. No problem, take out one of the rods, fix a long rod on your drill and spin it for a dozen second in the hole while moving the parts back and forth. Place back the rod a repeat the process for the other holes until the movement becomes smooth. You may want to make yourself a tool by warping one extremity of a 60 to 90mm rod in tape and tissue until it makes for a comfortable handle. It will be very useful to push rods out of their holes. Be cautious not to overheat the parts and induce play or you are good to print it again...

When the movement is smooth and without play, assemble the "middle" and "base" part with one of the springs and the 50mm bolt. Don't forget to add a washer to reduce the friction. Test that the spring is strong enough to push the junction, if so, you are ready for the next step.

## Step 6: Assemble the X Axis


To assemble the X axis, first put a nut on the tip of a bolt and insert it int the hexagonal hole of the "top" part. Like previously, use glue or a lighter if necessary.

Then, position the "top" part atop the "base" and "middle" assembly and place the 63.5 mm rods. Be cautious with the two rods on the bottom side, as they are difficult to remove when fully inserted. Keep a few mm exposed to catch them with a plier or use some longer rods for the adjustment process. Like previously, use a drill and a long rod to heat up the plastic and form the holes to exactly the right diameter. When the two parts slide smoothly add a spring, a 55mm bolt and a washer, and check that the spring is strong enough to push the assembly.

## Step 7: Assemble the Z Axis


To assemble the final axis, first insert the melt-inserts and the last nut in the "Z slider". Then place the slider in the assembly and add the 3x 52.5mm rods. Use the drill to adjust the hole size and add the spring and the last 55mm bolt.

At this stage, you can choose to glue the rods in place with a drop of cyanoacrylate at the extremities. Be aware that this will make it very difficult to disassemble, but it can also prevent the rods to come out after repeated use... You can also add a a bit of grease on the rods to make the movement smoother. None of those steps are strictly necessary.

## Step 8: Attach a Tool Holder

Micromanipulators are often used to take electrical contacts on microscopic electrodes, but that is not necessarily their only function (see my pipette adaptor (https://makerworld.com/en/models/208268#profileId-253155) for example). For this reason, I tried to make this design as versatile as possible using a fixation plate with 4x M3 melt inserts to allow you to design any tool head you may need. The plate holes are separated by 18mm horizontally and 15mm vertically.

To fix standard microelectronic tip holder, I also provide two different tool heads. One for straight tip holders with a degree of liberty in rotation and one for 90° bended tip holder.

In case you don't have (and need) a tip holder, you can make one with one of the 2mm rods, but this is a story for another Instructable.

## Step 9: (optional) Build the Tool Mounting Head

To build the "straight holder", you need to print 1x "straight holder base", 1x "straight holder arm", 1x "straight holder knob" and 2x "holder knob". Assemble the "straight holder knob" with a 20mm bolt and the two "holder knob" with 14mm bolts. Add two melt inserts to the arm and one to the base. Attach the "straight holder arm" to the "straight holder base" with the "straight holder knob" using a washer to ensure rotating the arm will not cause the knob to come lose.

For the 90° holder, you need 1x "90 holder" and 2x "holder knob". Add two melt inserts to the "90 holder" and assemble the knobs with 14mm screws.

Both types are secured to the micromanipulator using 8mm M3 screws.

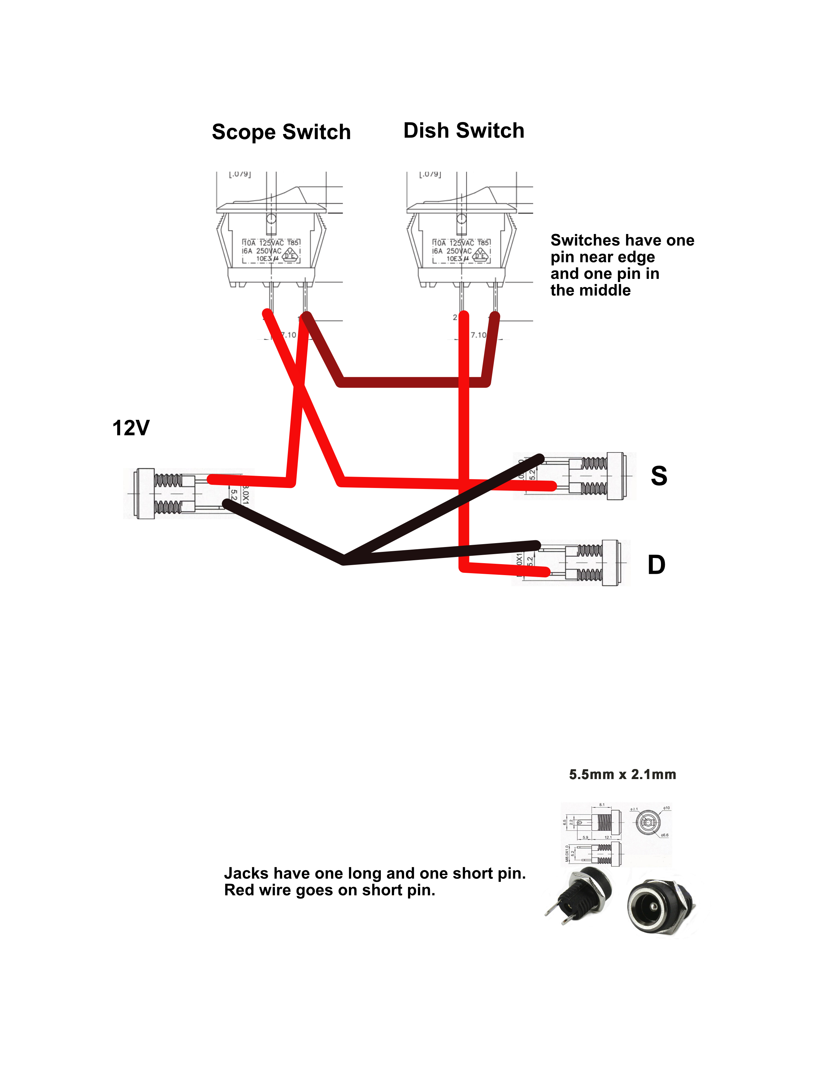
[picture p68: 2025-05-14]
Led light rings 2025/LED dish wiring diagram.jpg

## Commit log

2022-11-10 Add files via upload
    .stl files for building the DIY Calcium Fluorescence Scope.
    [C-Mount%20Collar%20(B).stl, C-Mount%20Lock%20NUt%20(C).stl, C-Mount%20Thread%20(A).stl, CourseFocusKnob.stl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]
2022-11-10 Add files via upload
    A suggested Bill of Materials for building the Fluorescence scope
    [EpiScopeBOM.xlsx]
2023-01-04 Tiny Micromanipulators
    [Tiny Manipulator Parts-2.stl, Tiny Manipulator Parts-3.stl, Tiny Manipulator Parts.stl]
2026-05-23 Add files via upload
    Parts for the electrode holder
    [Electrode Part A.stl, Electrode Part B.stl, Electrode Part C suction.stl, Electrode Part C.stl]
2026-06-02 Add files via upload
    added wire electrode instructions
2026-06-10 Add files via upload
    Simple CrawFly 3D model - logo
    [Surprising Curcan-3.stl]
